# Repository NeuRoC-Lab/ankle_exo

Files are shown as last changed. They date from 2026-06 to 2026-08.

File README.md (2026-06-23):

# ankle_exo
This repository stores the algorithms to operate The OpenExo Styled exoskeleton.

# instructions 

To run the Arduino-Teensy CAN sender receiver test do : 

(1) Connect each of the Arduino R4 and run `pio run -e can_module_arduinos_receiver` or `pio run -e can_module_arduinos_sender` for the receiver arduino and the sender arduino respectively 

(2) Connect one Teensy, run `pio run -e can_module_teensy_receiver` / `pio run -e can_module_teensy_sender` then do same as (1) for the remaining Arduino 

## CubeMars connection with the SN65HVD230 CAN Transceiver module + Arduino Uno R4

Run the Arduino code with `pio run -e arduino_can_cubemars` which will move the motor back and forth 

# A web documentation is available at [this website](https://oscartesniere.com/ankledocs/).

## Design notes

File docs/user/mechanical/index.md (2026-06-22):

Here is the information about the parts printed for the test bench and updates on the mechanical design of the ankle exoskeleton designed by the capstone team.

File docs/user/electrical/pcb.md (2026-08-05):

## The PCB design 

Our ankle exoskeleton design has different requirements than the original OpenExo design. In particular our exoskeleton differs on the following points : 

1. We are using 4x load cells, whereas the original board only accomodates 2x strain gauge amplifiers (INA125U)
2. Our design adds two AMT203 encoders which will most likely be operated over SPI. The original board does include SPI headers near the edge of the board, however the choice of SMT type headers make it incompatible with jumper wires. In addition our encoders work over 5V, which is incompatible with the 3.3V teensy.

Following those specific requirements, we brought the following changes to the board.

- Added two unidirectional voltage shifters for SPI operation at 5V (TXU0104PWR, TXU0304PWR)
-  Added 2 extra strain-gauge amplifiers (INA125U)
-  Used normal pin headers for SPI and included a second CS pin (because there are two encoders)

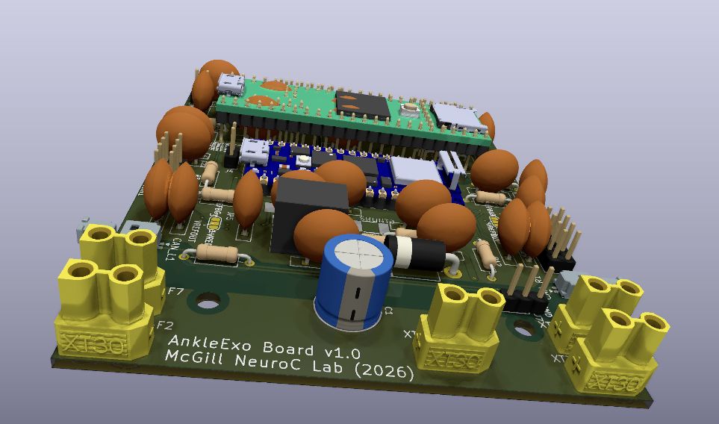
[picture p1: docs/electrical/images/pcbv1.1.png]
The PCB v1.1


A summary of the PCB's role in the ankle exoskeleton is shown in the following diagram : 

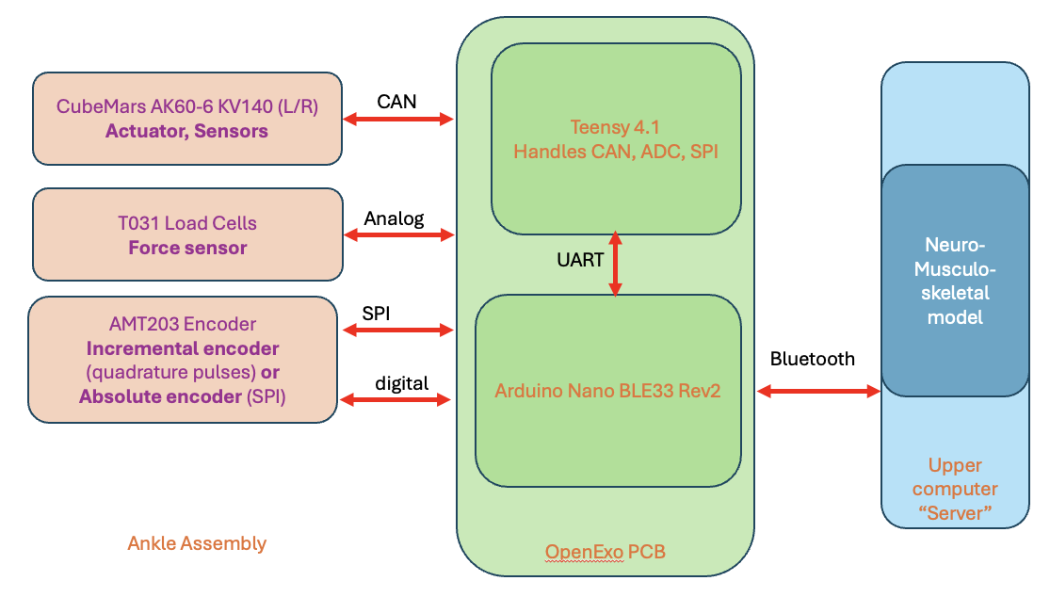
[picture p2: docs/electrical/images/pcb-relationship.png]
PCB diagram


Strain Gauge amplifier design :

The strain gauge amplifier instrumentation amplifier (INA125U) amplifies the voltage difference between the VIN- and VIN+

\[
V_o = IAREFF + G\times (V_+ - V_-)
\tag{1}
\]

Where the gain has expression : \(G = 4 + \frac{60k}{R_g}\)
We kept the original OpenExo gain resistor \(R_g = 470\) thus the gain is about 132.

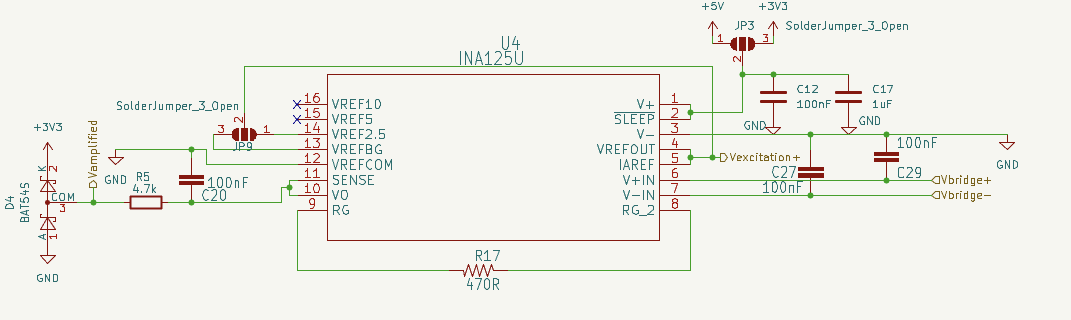
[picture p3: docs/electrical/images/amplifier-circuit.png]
Amplifier Design


In the original OpenExo design, the \(V_{REF}{OUT}\) pin is connected to \(V_{REF}{BG}\) which sets the excitation voltage to the bandgap reference voltage (1.24V).
The load cell datasheet suggests that a minimum of 5V excitation voltage may be used. Even when powering the INA125U the highest excitation voltage that can be achieved is 2.5V. 

For the iteration v1.0 I chose thus to add some flexibility to the choice of \(V_{REF}{OUT}\). Using a 3-pin SolderJumper (JP9,JP3) one can either set the excitation voltage to 1.24V or 2.5V, and the power pin of the IC can be set to 3.3V or 5V (JP3).

In order to allow for the possibility to use \(V_{REF}{5}\) or \(V_{REF}{10}\) I would have to power the chip with a voltage above 5V, or the onboard DC-DC regulator only supplies 5V. Another option could be to connect the INA125U directly to the battery power line but this might introduce some noise and transients from the battery loading the power lines.

The BAT54S is a Diode Array meant to clamp the output voltage in case it exceeds 3.3V, because the Teensy only accepts voltages up to 3.3V.

The `IAREFF` pin sets the voltage offset (see equation(1) ). Since the load cells will only be pulled (tensile force) in one _known_ direction, the polarity of the bridge sensing voltages can be set so that the output voltage will always be below `IARREF`. 
Then we can use a `IAREFF` value near 1.3V, and then the full band range will be between that value and 0V. 

`Load-cell full-scale differential output = sensitivity × excitation voltage`
The datasheet for the T031 load cells specifies 
Sensitivity = 1.0 mV/V nominal
Rated force = 1000 N 

Here is a table that gives the required gain for a given excitation voltage. The highest excitation that can be achieved with the onboard precision reference is 2.5 V, and with a gain of 132, that gives us a full-scale signal of 330 mV.

The desired gain is calculated as \(\text{Target gain} = \frac{3.3 V}{\text{full scale signal}}\)

| Excitation voltage | Load cell full-scale signal | Target gain for 0–3.3 V range | Target gain resistor value |
|-------------------:|----------------------------:|------------------------------:|:--------------------------:|
|            _2.5 V_ |                    _2.5 mV_ |                        _1320_ |          _45.6 Ω_          |
|              3.3 V |                      3.3 mV |                          1000 |           60.2 Ω           |
|                5 V |                      5.0 mV |                           660 |           91.5 Ω           |
|               10 V |                     10.0 mV |                           330 |          184.0 Ω           |

The two parameters that we can modify to increase the full scale signal range are 1) the gain and 2) the bridge excitation voltage

## Force conversion formula

We assume that the load cells are linear. Therefore, the following equality holds:

\[
\frac{V_{diff}(F)}{V_{diff,FS}}
=
\frac{F}{F_{FS}}
\]

where \(FS\) means **full scale**.

For example, the rated full-scale force of the load cell model is typically:

\[
F_{FS} = 1000\,\text{N}
\]

The full-scale differential voltage is given by:

\[
V_{diff,FS}
=
\text{sensitivity}
\times
V_{exc}
\]

Therefore, for an applied force \(F_{applied}\), the output voltage is:

\[
V_o(F_{applied})
=
V_{IAREF}
-
\text{Gain}
\times
\text{sensitivity}
\times
V_{exc}
\times
\frac{F_{applied}}{F_{FS}}
\]

Rearranging the equation:

\[
V_{IAREF} - V_o(F_{applied})
=
\text{Gain}
\times
\text{sensitivity}
\times
V_{exc}
\times
\frac{F_{applied}}{F_{FS}}
\]

Solving for the applied force:

\[
F_{applied}
=
\frac{
\left(
V_{IAREF}
-
V_o(F_{applied})
\right)
F_{FS}
}{
\text{Gain}
\times
\text{sensitivity}
\times
V_{exc}
}
\]

Thus, the applied force can be computed from the measured output voltage as:

\[
\boxed{
F_{applied}
=
\frac{
\left(
V_{IAREF}
-
V_o
\right)
F_{FS}
}{
\text{Gain}
\times
\text{sensitivity}
\times
V_{exc}
}
}
\]

## Effect of the INA125 input-offset voltage

In practice, the INA125 output does not necessarily equal \(V_{\text{IAREF}}\) when the load-cell bridge is perfectly balanced.

One cause is the INA125 input-referred offset voltage, denoted \(V_{\text{OS}}\). The datasheet specifies an input-offset voltage of up to approximately \(250\,\mu\text{V}\). This is a systematic offset, not noise.

The INA125 therefore behaves approximately as though \(V_{\text{OS}}\) were added to the true load-cell differential voltage:

\[
V_{\text{diff}}
=
V_{\text{diff,true}} + V_{\text{OS}}.
\]

The amplifier output becomes:

\[
V_o(F_{\text{applied}})
=
V_{\text{IAREF}}
-
G
\left(
V_{\text{diff,true}} + V_{\text{OS}}
\right).
\]

If the offset is ignored, the raw force calculated from the output voltage is:

\[
F_{\text{raw}}
=
\frac{
\left(
V_{\text{IAREF}} - V_o
\right)
F_{FS}
}{
G\,S\,V_{\text{exc}}
}.
\]

Substituting the amplifier equation gives:

\[
F_{\text{raw}}
=
\frac{
\left(
V_{\text{diff,true}} + V_{\text{OS}}
\right)
F_{FS}
}{
S\,V_{\text{exc}}
}.
\]

Since

\[
V_{\text{diff,true}}
=
S\,V_{\text{exc}}
\frac{
F_{\text{mechanical}}
}{
F_{FS}
},
\]

we obtain:

\[
F_{\text{raw}}
=
F_{\text{mechanical}}
+
\frac{
V_{\text{OS}}F_{FS}
}{
S\,V_{\text{exc}}
}.
\]

The input-offset voltage therefore produces an equivalent force offset:

\[
\boxed{
F_{\text{OS}}
=
\frac{
V_{\text{OS}}F_{FS}
}{
S\,V_{\text{exc}}
}
}
\]

Notice that this equivalent force offset does not explicitly depend on the amplifier gain. The gain increases both the useful signal and the output-referred offset by the same factor.

## Effect of residual cable tension

When the ankle exoskeleton is assembled, the Bowden cable may already apply a nonzero preload to the load cell. This residual force is denoted:

\[
F_{\text{residual}}.
\]

The total mechanical force measured by the load cell is then:

\[
F_{\text{mechanical}}
=
F_{\text{applied}}
+
F_{\text{residual}},
\]

where \(F_{\text{applied}}\) is the additional force of interest.

Including both the INA125 offset and the residual cable tension gives:

\[
F_{\text{raw}}
=
F_{\text{applied}}
+
F_{\text{residual}}
+
F_{\text{OS}}.
\]

Therefore,

\[
\boxed{
F_{\text{applied}}
=
F_{\text{raw}}
-
F_{\text{residual}}
-
F_{\text{OS}}
}
\]

or, written directly in terms of the measured output voltage:

\[
\boxed{
F_{\text{applied}}
=
\frac{
\left(
V_{\text{IAREF}} - V_o
\right)
F_{FS}
}{
G\,S\,V_{\text{exc}}
}
-
F_{\text{residual}}
-
\frac{
V_{\text{OS}}F_{FS}
}{
S\,V_{\text{exc}}
}
}
\]

## Practical zeroing procedure

In practice, \(F_{\text{residual}}\) and \(V_{\text{OS}}\) do not need to be determined separately. Both effects can be removed by recording the amplifier output after the exoskeleton has been assembled and placed in its reference unloaded state.

Let \(V_{o,0}\) be the output voltage measured in this reference state. It includes both the INA125 offset and the residual Bowden-cable tension:

\[
V_{o,0}
=
V_{\text{IAREF}}
-
G
\left[
S\,V_{\text{exc}}
\frac{
F_{\text{residual}}
}{
F_{FS}
}
+
V_{\text{OS}}
\right].
\]

When an additional force \(F_{\text{applied}}\) is present:

\[
V_o
=
V_{\text{IAREF}}
-
G
\left[
S\,V_{\text{exc}}
\frac{
F_{\text{residual}} + F_{\text{applied}}
}{
F_{FS}
}
+
V_{\text{OS}}
\right].
\]

Subtracting the two equations eliminates \(V_{\text{IAREF}}\), \(V_{\text{OS}}\), and the residual mechanical preload:

\[
V_{o,0} - V_o
=
G\,S\,V_{\text{exc}}
\frac{
F_{\text{applied}}
}{
F_{FS}
}.
\]

The corrected applied force is therefore:

\[
\boxed{
F_{\text{applied}}
=
\frac{
\left(
V_{o,0} - V_o
\right)
F_{FS}
}{
G\,S\,V_{\text{exc}}
}
}
\]

This equation assumes that the INA125 output decreases as the applied tensile force increases. If the output increases with force because the load-cell polarity is reversed, use:

\[
\boxed{
F_{\text{applied}}
=
\frac{
\left(
V_o - V_{o,0}
\right)
F_{FS}
}{
G\,S\,V_{\text{exc}}
}
}
\]

## ADC constraint limitation 

The teensy's ADC (for PCB versions v1.1.0 and earlier) and the Arduino Nano's ADC (for PCB versions v1.1.1 and above) can read analog voltages *from 0V to 3.3V* 

Therefore \(0 \le V_o(F_{\text{applied}}) \le 3.3\)

\[ \iff \frac{V_{\text{IAREF}}\cdot F_{\text{FS}}}{G\cdot S  \cdot V_{exc}} \ge F_{\text{applied}} \ge \frac{(V_{\text{IAREF}}-3.3)\cdot F_{FS}}{G\cdot S  \cdot V_{exc}}\]

An example for the following configuration : 

| Gain (G) | Maximum tensile force \(F_{\min}\) | Maximum compressive force \(F_{\max}\) |
| -------: |-----------------------------------:|---------------------------------------:|
|     6004 |              \(-83.28~\mathrm{N}\) |                  \(+26.65~\mathrm{N}\) |
|     1204 |             \(-415.28~\mathrm{N}\) |                 \(+132.89~\mathrm{N}\) |

Note that compression and tension are defined visually the following way. 

Because the motor actively pulls on the load cells, the expected tensile-force range is greater than the expected compressive-force range. The INA125U reference voltage was therefore selected so that a larger portion of the ADC input range is allocated to tensile-force measurements.

The value of \(V_{\mathrm{IAREF}}\) was set to \(2.5~\mathrm{V}\). With an ADC input range of \(0\text{–}3.3~\mathrm{V}\), this provides \(2.5~\mathrm{V}\) of output range below \(V_{\mathrm{IAREF}}\) and \(0.8~\mathrm{V}\) above it. This choice is appropriate if tensile loading causes the INA125U output voltage to decrease. If tensile loading instead causes the output voltage to increase, \(V_{\mathrm{IAREF}}=1.24~\mathrm{V}\) would provide greater tensile-force headroom.

The higher-output range of the INA125U was not used because the amplifier output is not inherently limited to the ADC’s maximum allowable input voltage of \(3.3~\mathrm{V}\). An excessive load could therefore overdrive, and potentially damage, the ADC input unless an additional clamping or protection circuit is used.

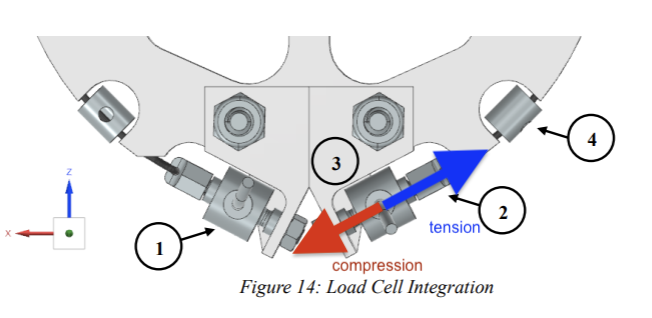
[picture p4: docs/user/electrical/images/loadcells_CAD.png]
load cell CAD

## Pinout of the PCB 

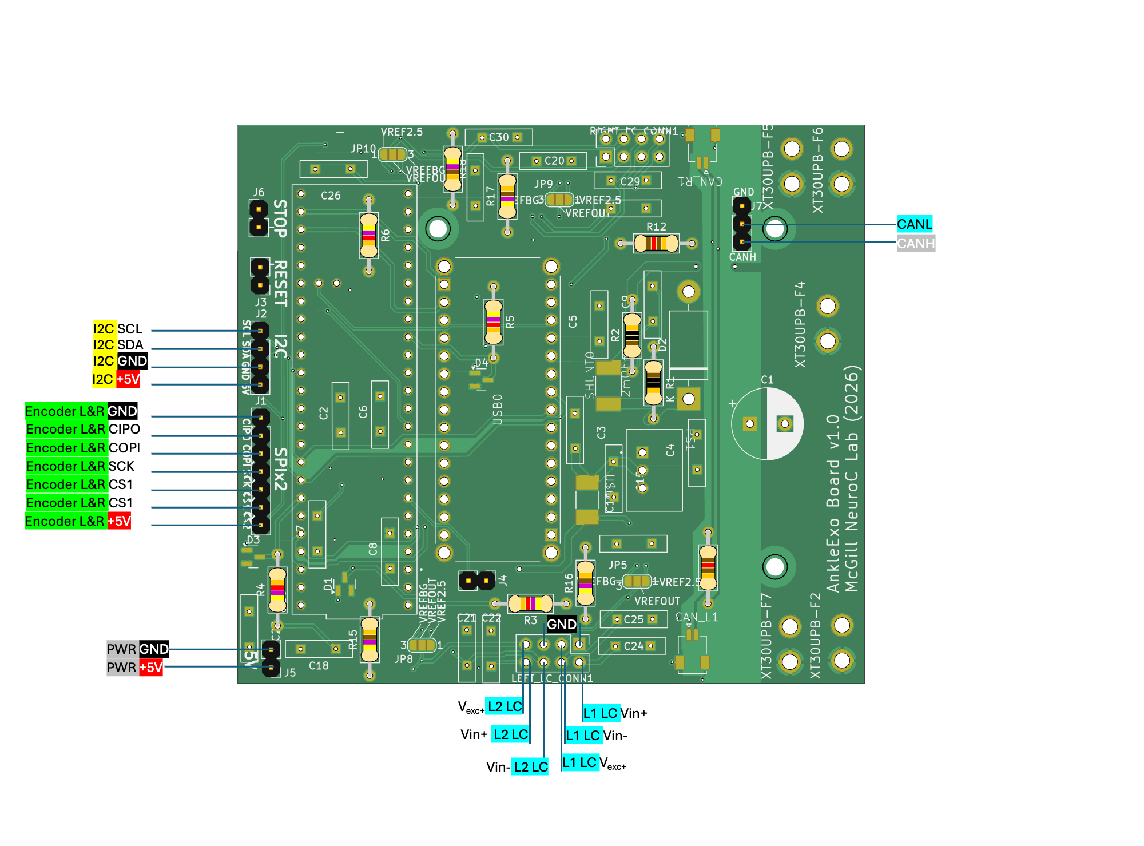
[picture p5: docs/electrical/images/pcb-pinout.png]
Pinout


Pinout for the load cells connectors : 

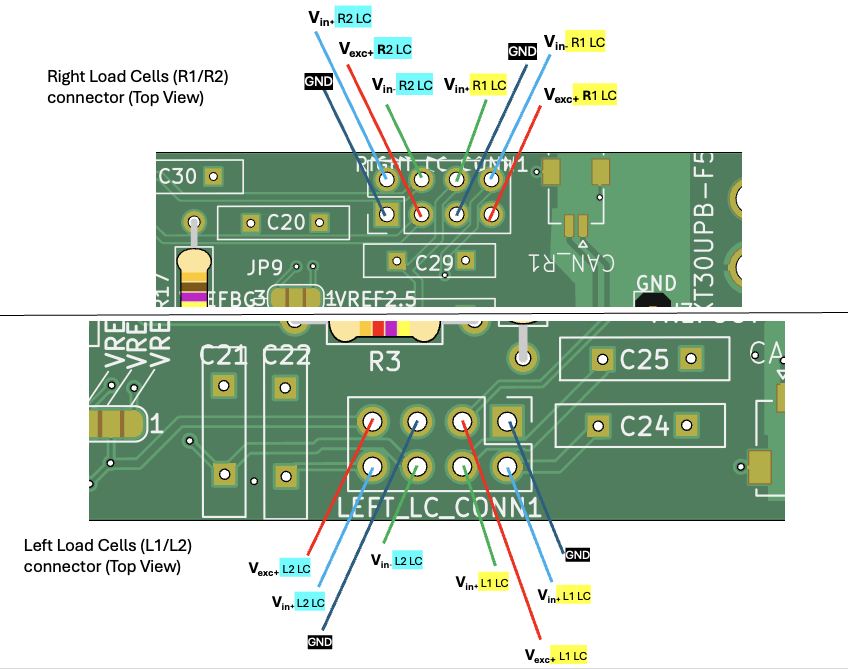
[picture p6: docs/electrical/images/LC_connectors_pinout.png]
Load Cells Pinout

## PCB changelog 

#### 26/06 (version 1.0.0)

* Refactored labels for INA solder jumpers by aligning the labels on a "45degrees" plane so that we can distinguish those labels from other things on the board (clearer for reading)
* Added a solder jumper for INA excitation voltage to choose between the INA voltage reference (2.5v/BG) or 5V from PCB regulator
* Added a solder jumper to choose whether to connect the Teensy's VIN to the board (so that we can use USB)

#### 03/07 (version v1.0.1)

* Modified the Teensy 4.1 footprint to include two 1x24 PinSocket rows so that we can include the pin socket soldering into PCBA for JLCPCB
* Added a status LED for the 5V power line
* Make sure to check for unconnected zones 
* Modified the pinout order for the SPI header (it is now from left to right `GND`,`SCK`,`COPI`,`CIPO`,`CS1`,`CS2`,`5V`)
* Make sure to check the option `Subtract soldermask from silkscreen` : this will tell KiCad to _automatically remove silkscreen graphics/text wherever they overlap exposed copper pads_ which might otherwise cause manufacturing issues
* **MAIN PATCH : **  Re-routed the TXU304 and TXU0104 input  / output pins to resolve mismatch in version v1.0.0. The inputs were misconnected to outputs which made the SPI non functioning on version v1.0.0. _The SPI bus has fixed direction ports (COPI, SCK, CS go from controller to peripheral, while CIPO goes from peripheral to controller) but the order was mismatched in version 1.0.0_

Before the patch `.1`
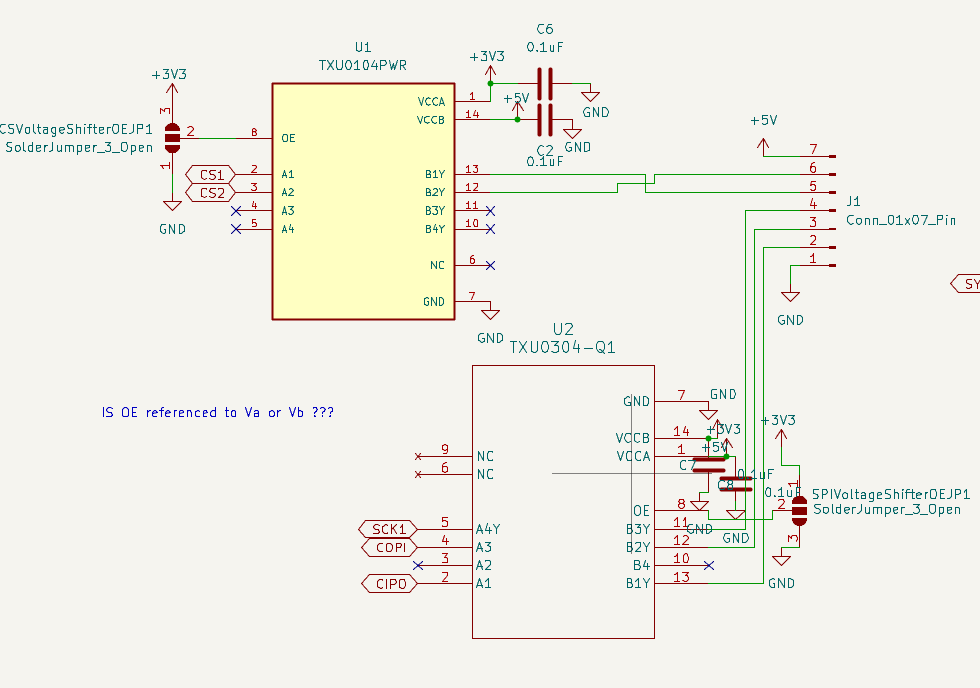
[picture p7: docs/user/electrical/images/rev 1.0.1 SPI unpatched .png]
SPI before patch 1.0.1

After the patch `.1`
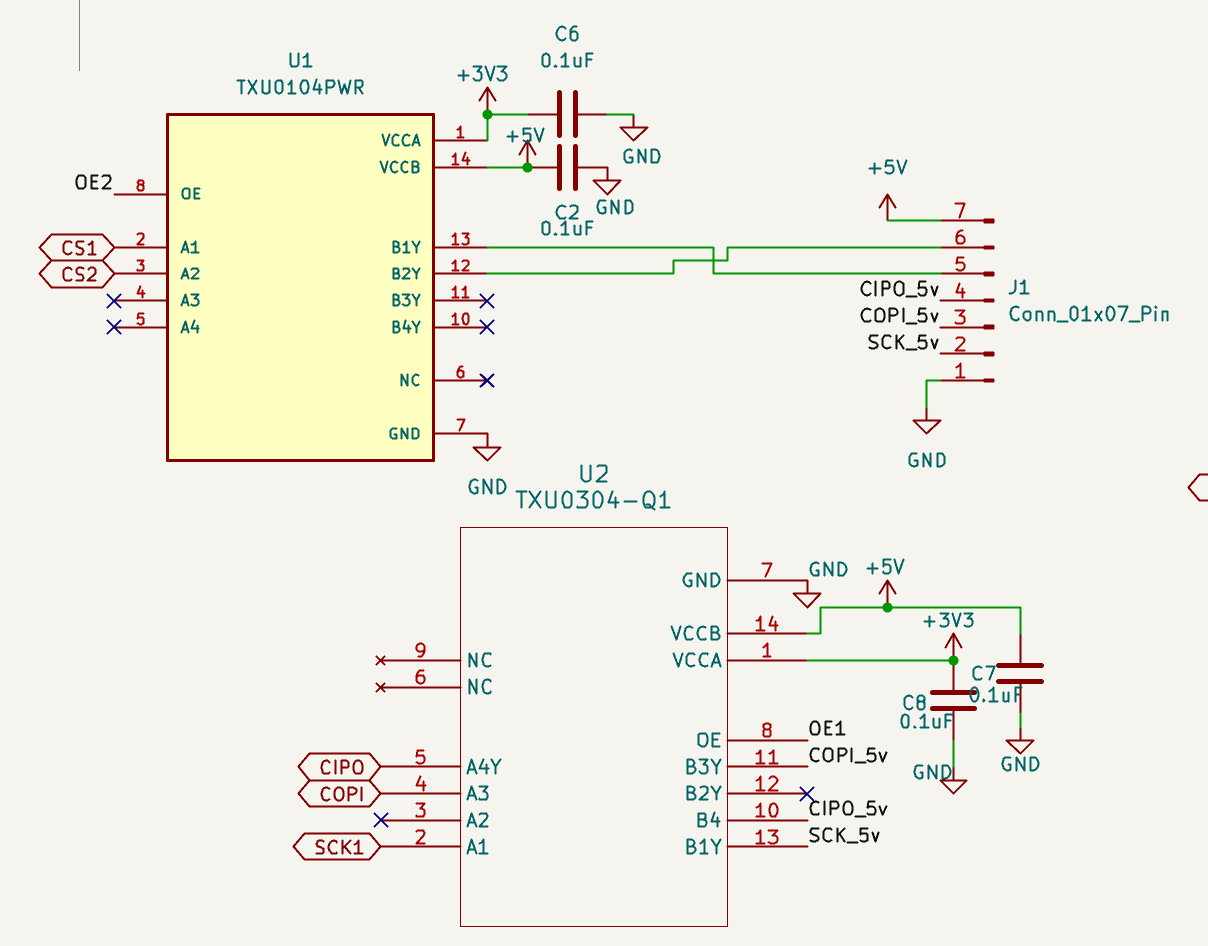
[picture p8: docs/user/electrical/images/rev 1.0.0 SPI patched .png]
SPI after patch 1.0.1


#### 04/07 (version v1.0.1)
* connected excitation voltage outputs of the 4 INA125U to Teensy's Analog inputs so that the Teensy can ensure the INA125Us are properly wotking and that these match the settings in Board.h

#### 17/07 (version v1.1.0)

* Replaced erroneous Arduino Nano (BX00028=Nano Every) symbol+footprint with corresponding model (the BX00071=Nano BLE33 R2). Check that the older versions (<v1.1.0) are not affected, especially UART b/w Teensy and Nano
* Redesigned the load cell sampling circuit to use the Arduino Nano's builtin SAADC in differential mode. The advantages are :
  * The Teensy 4.1's analog pins are known to be noisy so the Nano naturally becomes a more stable option 
  * The differential mode (where IN+=Vexc and IN-=INA125U output) simplifies the `Board.h` configuration. The code no longer needs to know what voltage is each IAREF at, since the differential ADC extracts the differential voltage 
  * The differential mode also improves signal integrity by rejecting the common-mode noise picked up by the lines on the PCB.
  * The differential mode eliminates any IAREF voltage drifts / offsets _ACCROSS_ and _WITHIN_ all four INA125Us. The code assumed that the IAREF voltages were exactly 2.5V or 1.24v but in practice soldering quality and trace impedance can affect that by introducing some variability between the IAREF of each respective INA125U
  * The Arduino Nano's SAADC features a PGA stage which makes this setup more flexible to changing `Rg` gain resistors. We can optimize the dynamic range to improve resolution.
* Redesigned the `LEFT_LC_CONN` and `RIGHT_LC_CONN` pinout so that 1) they are identical (versions < v1.1.0 had distinct pinouts) 2) they are _SYMETRICAL_ which means the 2x4 connector can safely be flipped, only the load cell will be swapped. 
PCB assembly list : 

https://jlcpcb.com/help/article/how-to-generate-the-bom-and-centroid-file-from-kicad

### 23/07 (v1.1.0)

* Fixed XT30 connector pin mismatch on kicad which resulted in \(V_{batt}\) and \(GND\) nets not being actually electrically connected to the XT30 pins on the board. For this I renamed the pin names on the symbol from "P" and "N" to 2 and 1 respectively, as required in the footprint 
* Replaced the imported Teensy symbol which made some pins not properly connected 
* Remade Solder jumper annotations pertaining to each of the four amplifiers more consistently (INA_PWR_xx, INA_EXC_xx, INA_REF_xx) for 1,2,3,4
* Converted 3-pins solder jumpers to 2-pins solder jumpers to avoid harming Nano ADC by connecting it to 5V

### 25/07 (v1.1.1)
* Replaced the P78E05-1000 with a [Würth Elektronik pin-compatible equivalent](https://www.we-online.com/components/products/datasheet/173010535.pdf?srsltid=AfmBOoqXnjU4nN0V3SnTI2uxeimFK-YTeBzOPeDcg751XvU_F-sQBI_F).
  * MINOR ROUTING FIX (schematics/pcb) : While the pinout for P78E05-1000 is 1-Vin, 2-GND, 3-Vout, the v1.1.0 board that was obtained through JLCPCB (the second one) had 3) have pin 2 and 3 swapped and pin 1 not actually connected to Vin (battery). The routing was redone properly, and bulk capacitors were placed at input and output of the DC-DC converter

* MINOR WIRING FIX (schematics/pcb) : The BAT54S clamping diode array was replaced with a more accurate one (BAS70-04). The cathode and anode were swapped in the old version, which has been fixed when adding the replacement diode array.
* The Teensy 4.1's footprint and symbol was modified and I principally removed unused THT pins like VUSB,T+/T-,D+/D- and otherswhich would have overlapped with some components under the Teensy

<iframe
src="https://oscartesniere.com/3dviewer/viewer/embed.html#model=https://oscartesniere.com/3dviewer/models/AnkleExov1_1_0.glb"
title="AnkleExo PCB v1.1.0"
width="100%"
height="700"
style="
display: block;
width: 100%;
border: 1px solid #cccccc;
border-radius: 8px;
"
loading="lazy"
allowfullscreen>
</iframe>

<iframe
src="https://oscartesniere.com/3dviewer/viewer/embed.html#model=https://oscartesniere.com/3dviewer/models/AnkleExov1_1_1.glb"
title="AnkleExo PCB v1.1.1"
width="100%"
height="700"
style="
display: block;
width: 100%;
border: 1px solid #cccccc;
border-radius: 8px;
"
loading="lazy"
allowfullscreen>
</iframe>

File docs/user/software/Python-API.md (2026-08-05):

## Python API

A self-contained Python API has been written to interface the exoskeleton from a BLE compatible device in Python.

The file to use is `src/python-scripts/SingleLeg/single-exo.py`

The main `Exoskeleton` class supports context management framework, which internally handles connection to and disconnection from the BLE-enabled Arduino Nano

A typical script skeleton loooks like this : 

```python
from single-exo import Exoskeleton
# assumes your python file is in `src/python-scripts/SingleLeg`

with Exoskeleton() as ankle_exo:
    # your code goes here, connection and disconnection is being handled internally 
    pass
```

Please see the available functions to read from the sensors and to send commands to the Motors.

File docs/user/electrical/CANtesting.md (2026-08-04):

### Validation of the onboard CAN

An external CAN module was used to test the proper operation of the CAN bus. The CAN bus was then made of two nodes : the SN65HVD230 transceiver on the PCB, and another SN65HVD230 transceiver on the external module.
> Note that because the PCB already includes a 120 \(\Omega\) termination, you MUST unsolder the 60 \(\Omega\) resistor on the external CAN transceiver module (use a voltmeter to identify which resistor to remove among the two. The other one is usually 10k \(\Omega\))

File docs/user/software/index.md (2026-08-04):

The software layer works as follows : 
* The Teensy 4.1 and Arduino Nano BLE33 Rev2 make part of the PCB software stack
* The main "server" running torque moment generation is a separate entity 

## Teensy and Arduino Nano programing environment and workflow :

### Platformio 

We chose platformio (abbreviated `pio`) for it's seamless integration with both the Arduino Nano and the Teensy.
The Arduino IDE supports both boards and architecture, however pio provides useful features key to our development : 
- All-in-one compile-upload-monitor pipeline for fast development
- Configurable environments to distinguish scripts that are to be run on the Teensy vs those to be run on the Arduino. The environments are defined in `platformio.ini`
- Easier project management for multiple sketches. The CLI-based nature of pio allows us to easily integrate version control (git) 

To run an environment (ex `myenv`) run in the same directory as `platormio.ini` the following command : `pio run -e myenv`

To monitor a specific device (`myport`) over the serial monitor run `pio device monitor --port myport`. To get the list of available ports run `ls /dev/cu*`

#### Platformio setup 

Platformio can be installed as a standalone application [`platformio cli`](https://docs.platformio.org/en/latest/core/index.html) which gives access to a command line interface for running direct commands. It is lightweight and does not rely on an overlaying IDE, however you must be familiar with CLI and know the commands to run for compiling/uploading/monitoring

Platformio is also available as an integration into popular IDEs like VScode, CLion [`platformio-ide`](https://docs.platformio.org/en/latest/integration/ide/pioide.html#pioide). We recommend using VScode because the graphical interface is easy to navigate through. 

To install platformio on vscode, locate the platformio plugin in the marketplace 

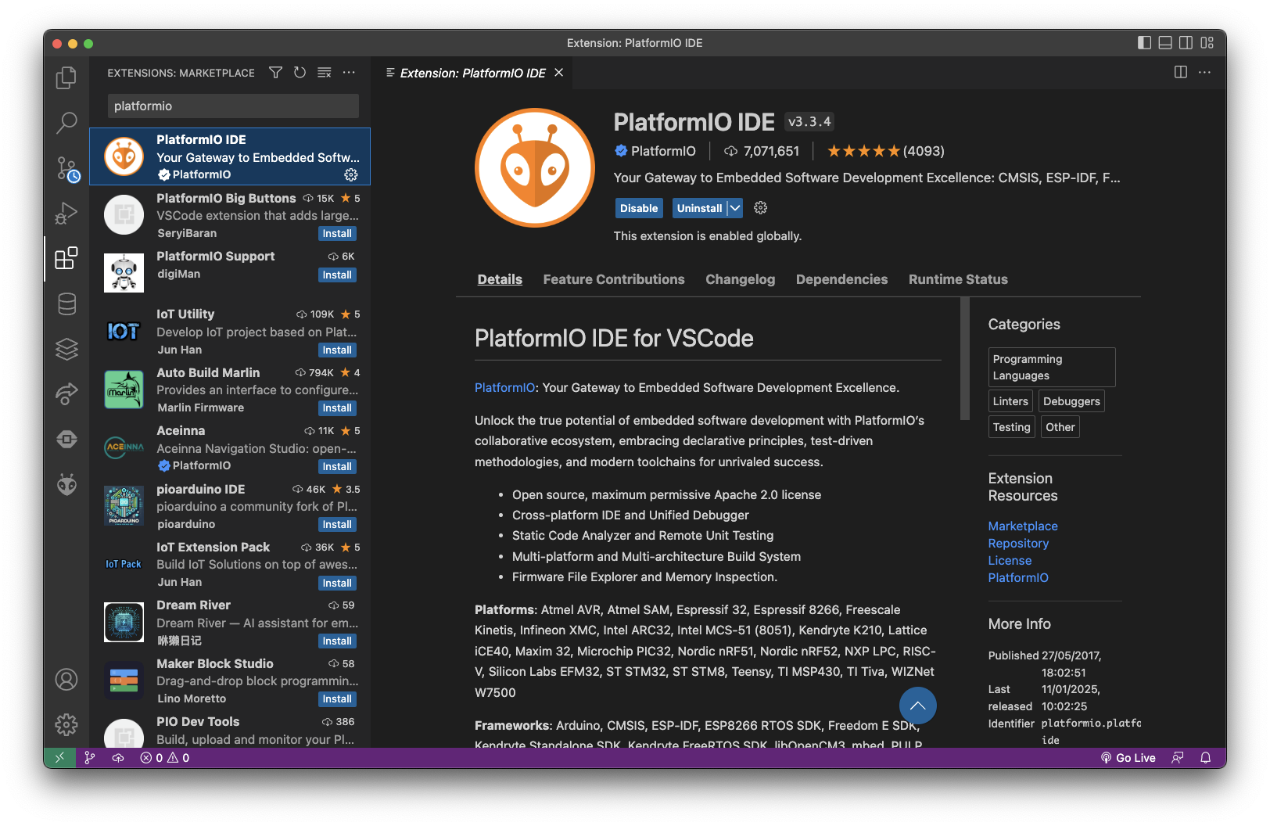
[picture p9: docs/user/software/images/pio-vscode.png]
VScode installation of platformio


To install platformio on CLION, follow the instructions [here](https://www.jetbrains.com/help/clion/platformio.html#debug-prj)

### Setting up the Arduino IDE for compiling, uploading and monitoring the Teensy 4.1

_For reference : https://www.pjrc.com/teensy/tutorial.html_

The Arduino IDE doesn't provide a built-in board manager for the Teensy 4.1 board, so the first time setting up the Arduino IDE for the project you'll need to add this custom board manager URL from PJRC :

In the `Additional boards manager URLs` (`File > Preferences`) text box paste the following URL : 

`https://www.pjrc.com/teensy/package_teensy_index.json`

Wait for the IDE to install the board package, then make sure to choose the port labelled `Teensy 4.1`. Another port will show up when you plug the Teensy on your computer, but do not choose this one. 

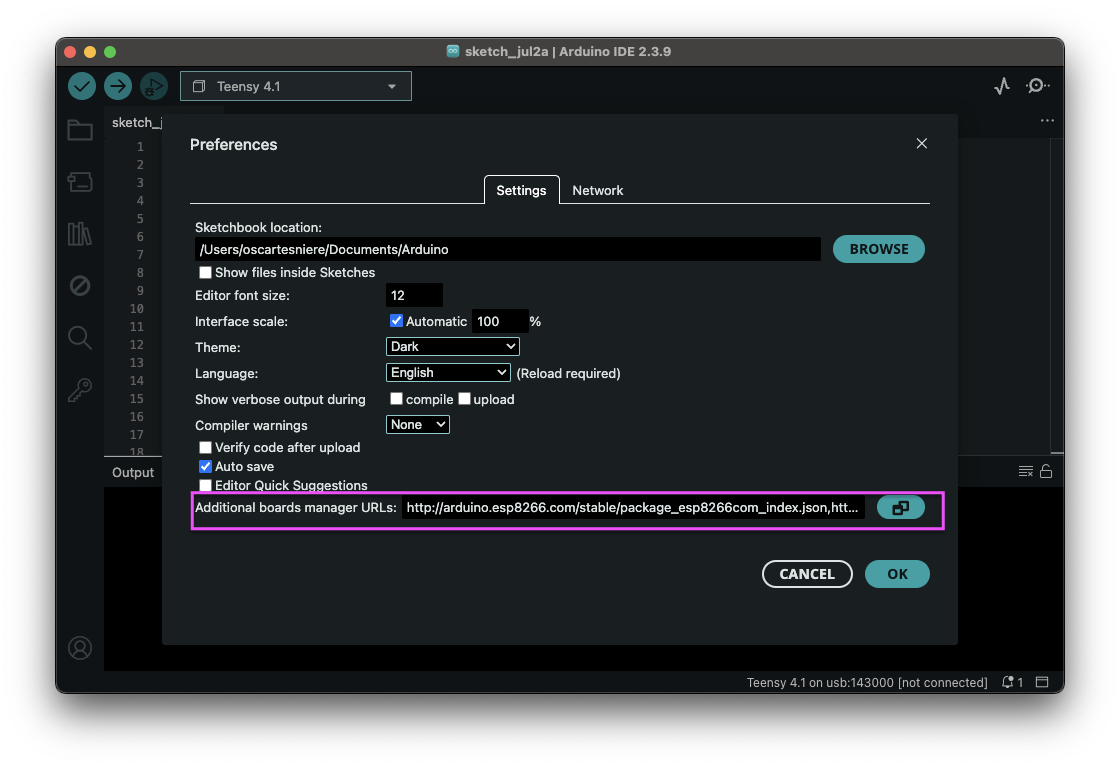
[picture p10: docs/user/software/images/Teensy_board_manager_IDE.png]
Port selection


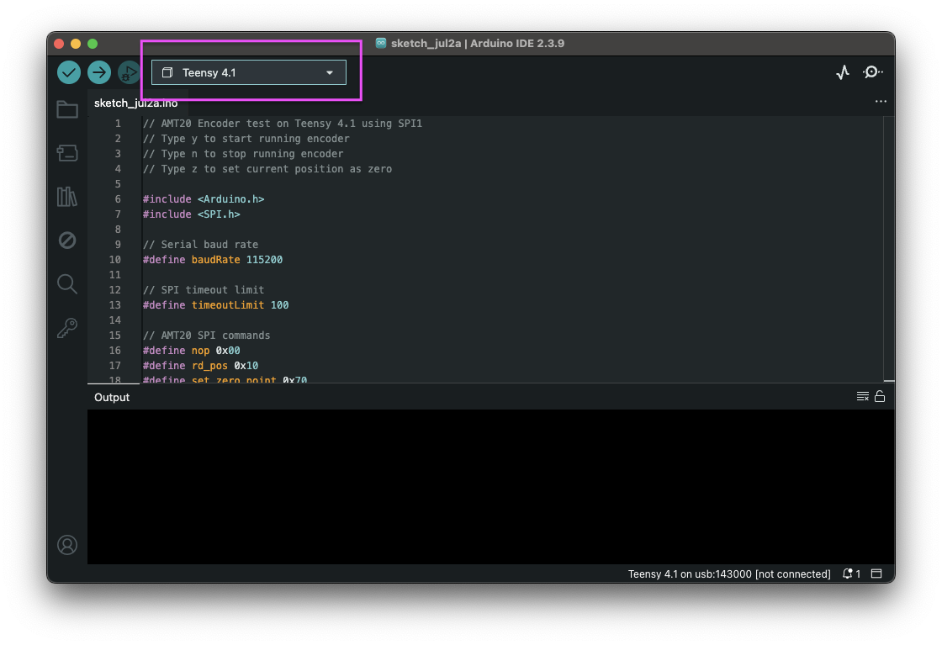
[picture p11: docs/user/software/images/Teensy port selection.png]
Board Manager setup


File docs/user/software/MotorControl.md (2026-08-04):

### Motor control theory 

The user-commanded position, velocity, torque, proportional gain, and derivative gain are restricted to a commanded operating range, referred to as the **software constraint set**, (\mathcal{S}).

A second, extended admissible range is defined as the **running constraint set**, (\mathcal{R}). This range represents the absolute limits within which the motor is permitted to operate based on its measured state. The two constraint sets satisfy

\(\mathcal{S}\subseteq\mathcal{R}\)

and, when the running constraint is strictly wider than the software constraint,

\(\mathcal{S}\subsetneq\mathcal{R}\)

Consequently, a user command must satisfy

\(\mathbf{u}_{\mathrm{cmd}}\in\mathcal{S}\),

whereas the measured motor state must remain within

\(\mathbf{x}_{\mathrm{motor}}\in\mathcal{R}.\)

The region (\mathcal{R}\setminus\mathcal{S}) provides a recovery margin that accommodates tracking error, system dynamics, and externally imposed motion while preventing the user from directly commanding the motor near its absolute operating limits.

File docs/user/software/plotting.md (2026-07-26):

## Reference Page for Real-Time Sensors Plotting Scripts

The real-time plotting of the exoskeleton sensors and motors is achieved using Python 
To check for the list of ports in CLion IDE, use python -m serial.tools.list_ports

The result for a one leg setup can be found through the unified.py script under software/src/python-scripts
It plots 6 graphs: 

- encoder angle
- encoder velocity
- cable tension 1
- cable tension 2
- motor position
- motor velocity

Challenges encountered and solution process:

1. Find a way to control the motor while the plot is running

- UI slider
  - Pros: easy to use for testing purposes
  - Cons: only temporarily needed feature
- Import threading to send commands via the terminal
  - Pros: same way to control motor as the motor script alone
  - Cons: not practical at all if printing data on the terminal 
- Using Teensy and Nano at the same time (plot from reading Nano data, control motor by sending commands to Teensy)

2. Plot fast and smoothly enough

- Replace 
  raw = ser.readline().decode(errors="ignore").strip()
  with
  while ser.in_waiting:
  raw = ser.readline().decode(errors="ignore").strip()
- Telemetry library?

3. Noise in one load cell caused by crosstalk and wiring/PCB issues

4. Encoder noise when motor is turned on but with a zero velocity

5. Encoder random spikes caused by invalid reading returns the uint_16_max
- When there is an invalid reading, plot the previous valid reading

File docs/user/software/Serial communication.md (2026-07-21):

### Serial communication between the Teensy 4.1 and the host computer

!!! info "Note for later iterations" 
    The use of Serial communication (UART) seemed like an ideal choicen for us because 1) it is easier to implement than SPI 2) we can easily transpose it to Bluetooth later on

## Teensy payload formating

A typical packet from the Teensy looks like this, as seen from the Serial Monitor

```python
 {
    "LLC1":2.512674,
    "LLC2":2.532015,
    "RLC1":0.032234,
    "RLC2":0.030623,
    "LENC":28671,
    "RENC":65295,
    "MOTORS":[{"MTR_ID_DEC":2,"MTR_POS_RAD":0.476654,"MTR_VEL_RADS":0.032967,"MTR_TRQ_NM":-0.032967,"MTR_TEMP_DEG":64,"MTR_ERR_DEC":0}]
}
```
the main fields are : 

* `LLCx` : left load cell x (1 or 2)
* `RLCx` : right load cell x (1 or 2)
* `LENC` : left encoder count
* `RENC` : right encoder count
* `MOTORS` : motors field, contains a list of motor telemetry data (one per each) with keys `MTR_ID_DEC`, `MTR_POS_RAD`, `MTR_VEL_RADS`, `MTR_TEMP_DEG`, `MTR_ERR_DEC`

On python, you need to do the following to retrieve data (See `testUart.py` for an application)

1. Parse the line from the Serial with `line = Serial.readLines('\n')` 
2. Parse the JSON to convert the string into a dictionnary-like array with `packet = json.loads(line)`
3. Extract individual fields with `.get()` method. For example :
```python
left_load_cell = packet.get("LLC1")  # left load cell 1 voltage
right_encoder = packet.get("LENC") # left encoder count
```

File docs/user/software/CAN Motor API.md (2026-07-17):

### Usage of `CANMotorMIT.h` and `ServoCANMotor.h` erre— CAN Motor API

1. In both MIT and Servo modes, auxiliary libraries such as `SerialMotorControl.h` use the generic `CANController` type name for the selected motor controller.

   Therefore, after including the appropriate controller header, define `CANController` as an alias for the platform-specific implementation.

   For MIT mode with a Teensy 4.1:
```Cpp
#include "CANMotorMIT.h"
using CANController = CANMotorMIT_Teensy;  
```

   When using an Arduino UNO R4 instead:

```Cpp
using CANController = CANMotorMIT_Renesas;
```

   For Servo mode with a Teensy 4.1:

```Cpp
#include "ServoCANMotor.h"
using CANController = ServoCANMotor_Teensy;
```

   When using an Arduino UNO R4 instead:

```c++
using CANController = ServoCANMotor_Renesas;
```

2. In MIT mode specifically, the user must define:

    * the software command constraints;
    * the motor running constraints.

   These values should be configured in `MotorConfig.h`.

3. Create a `MotorCmd` object that will store the commands sent to the motor.

   Example for MIT mode:

```c++
MotorCmd motor1Cmd {
      .position = 0.0f,
      .velocity = 0.0f,
      .torque = 0.0f,
      .kp = 0.0f,
      .kd = 0.0f
   };
```

4. Instantiate a `CANController` object.

   Example for MIT mode:

```c++
CANController motor(
       MOTOR_ID,
       &motorParams,
       &motorSoftwareConstraints,
       &motorRunningConstraints,
       motor1Cmd,
       printRate
   );
```

   The arguments are:

    * `MOTOR_ID`: the motor CAN ID. It can be checked or configured using the CubeMars Upper Computer software.
    * `motorParams`: the nominal motor communication parameters.
    * `motorSoftwareConstraints`: the limits applied to commands before they are sent to the motor.
    * `motorRunningConstraints`: the safety limits checked against motor feedback.
    * `motor1Cmd`: the `MotorCmd` object containing the current user command.
    * `printRate`: the motor status will be printed to the Serial Monitor once every `printRate` received frames.

   The Servo-mode constructor may use a different set of arguments because software and running constraints are currently specific to the MIT controller.

5. Include `SerialMotorControl.h` to enable control through the serial interface:

```c++
   #include "SerialMotorControl.h"
```

   Include this header only after the `CANController` alias and motor object have been defined, if the library depends on them.

6. Create the serial controller object:

```c++
   SerialMotorControl serialControl(Serial, motor1Cmd, motor);
```

7. In `setup()`, initialize the motor controller:

```c++
motor.begin();
```

   Reset and enable the motor using:

```c++
   if (!motor.resetMotor()) {
       Serial.println("Failed to start motor");
   } else {
       Serial.println("Motor started successfully");
   }
```

8. In `loop()`, call the following functions to process CAN communication and serial commands:

```c++
   void loop()
   {
       motor.update();
       serialControl.update();

       delay(10);
   }
```

   The delay is currently required for reliable serial command handling and should not be removed until the timing behavior has been investigated.

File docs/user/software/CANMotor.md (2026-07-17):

## Software layout for the project 

### CANMotor class

The `CANMotor` class is the main class used to interface the motor. 

As of now because we are having issues interfacing the encoders with the Teensy over SPI (voltage conversion related) I gave the possibility 
for the user to control the AnkleExo PCB using 1) the Teensy and 2) with the Arduino Uno R4. It is necessary to split the implementation for the Uno R4 and the Teensy 4.1 because these two boards use different CAN Controller libraries.
The Arduino uses `Arduino_CAN.h` while the Teensy currently uses `FlexCAN_T4`. For that reason I created two subclasses for each board so that one can use one or the other board as they wish.

Note that because only the Teensy 4.1 and Arduino UNO R4 boards have an integrated CAN controller other regular boards like the Arduino UNO R3 _cannot_ be used for this class.

For the wiring, please refer to `board.h` and the `electrical` section of this documentation. It differs from board to board.

A representative OOP diagram of the `CANMotor` class and it's two subclasses `CANMotor_Teensy41`, `CANMotor_Renesas` is shown below

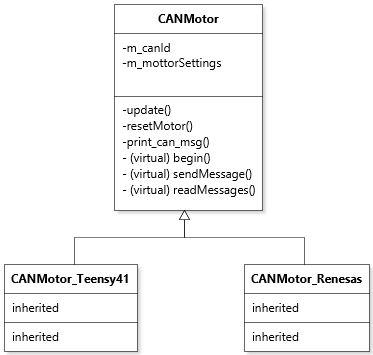
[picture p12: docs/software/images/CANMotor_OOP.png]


To run the unified CAN controller example code (`CAN_unified.cpp`) you will need to run the pio environment `CAN_teensy41` or `CAN_uno_r4` depending on which board you are using. 
As a reminder, the general format to run an environment in platformio is `pio run -e yourenvname` where `yourenvname` is the target environment. 

#### Design update (25/06)

After the Servo mode was successfully tested on June 24th we are now implementing a separate class for the MIT and Servo mode. Those supercless are `CANMotorMIT` (MIT mode) and `ServoCANMotor` (Servo mode). Note that these two classes need to been validated again 

| Class                   | Mode | Board          | Platformio Environment        |
|-------------------------|-----:|:---------------|-------------------------------|
| `CANMotorMIT_Teensy`    |  MIT | Teensy 4.1     | `pio run -e MIT_CAN_teensy41` |
| `CANMotorMIT_Renesas`   |  MIT | Arduino Uno R4 | `pio run -e MIT_CAN_uno_r4`   |
| `ServoCANMotor_Renesas` | Servo | Arduino Uno R4 | `pio run -e Servo_CAN_uno_r4` |
| `ServoCANMotor_Teensy`  | Servo | Teensy 4.1     | NOT IMPLEMENTED YET           |

The following commands can be run (rightmost command) to execute the MIT/Servo demo code on the Teensy/Arduino Uno R4. 
Note the following : 

* You must wire the CANTX/CANRX wires accordingly to the Teensy or Arduino UNO R4.

* For the Arduino 

  | OpenExo PCB                     | Arduino |
  |---------------------------------|--------:|
  | CANTX _through voltage divider_ |     D10 |
  | CANRX                           |     D13 | 
  | GND                             |     GND | 
  | 3.3V                            |   3.3V  | 

* For the Teensy

| OpenExo PCB                     | Arduino |
|---------------------------------|--------:|
| CANTX  |     D22 |
| CANRX                           |     D23 | 
| GND                             |     GND | 
| 3.3V                            |    3.3V | 

#### Serial communication 

The serial communication to control the motor works as follow : 

##### MIT mode

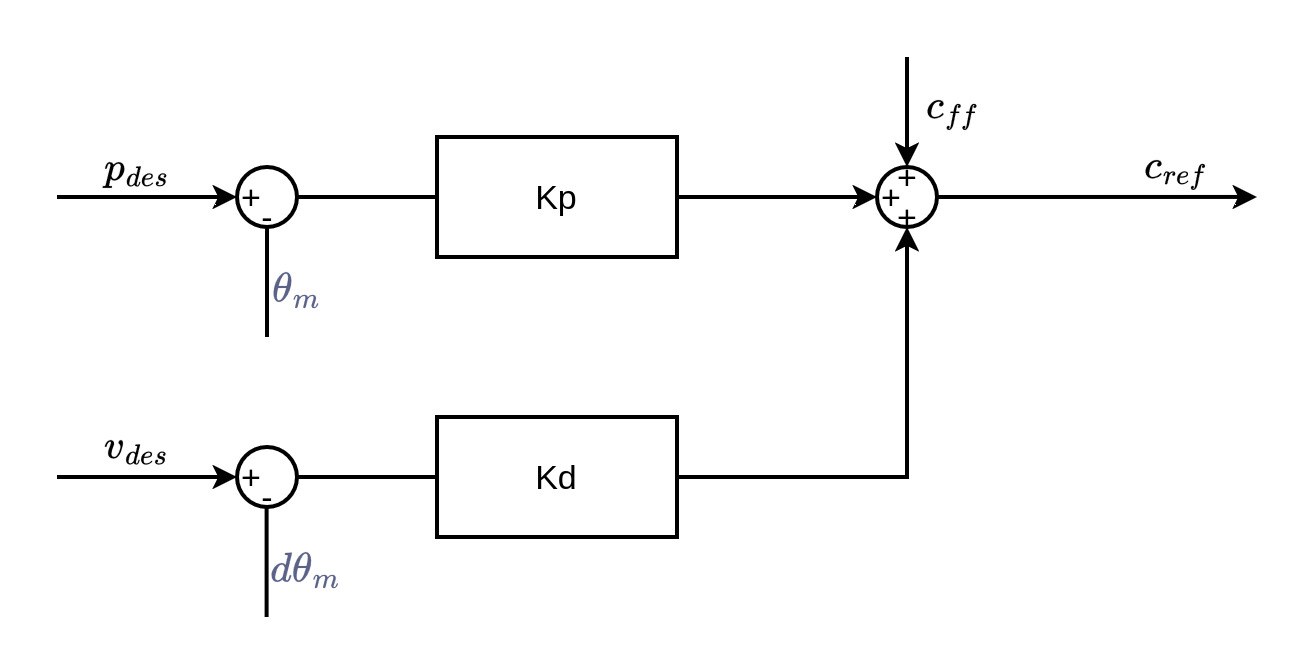
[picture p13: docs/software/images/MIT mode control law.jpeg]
MIT control law from SITODRIVE


\(c_{ff}\) value is usually the sum of the current required to offset the friction of the actuator and the current value calculated by the robot dynamics

When the kp and kd values are both 0, the rotational stiffness and damping are both 0, which is equivalent to the current mode, and the phase current can be directly controlled:

Increasing the feedforward torque \(c_{ff}\) will offset the necessary torque to overcome the static friction. As a consequence the motor is set into motion easier. 

References from [sito drive for the MIT actuator control mode](https://docs.sitodrive.com/Joint_Actuator_User_Documentation/Detailed_explanation_of_control_mode/MIT_mode)

Note : setting kd to wero will make the motor oscillate about the target position which is not recommended

* `start id xx` : start the motor 
- To enable the control loop, after a "crash" wherein the motor disables itself after a fault was detected

* `stop id xx` : disable the control loop (the motor is in idle mode, and keeps sending telemetry data but there is no actuation. note you can still set MIT parameters)
- To exit idle mode, enter the `start` command. 

* `zero id xx` : resets the motor's encoder position to 0 at the current position. 

`set` | `id xx`: 

  - `pos x.x` : position (in radians from -12.0 to +12.0)
  - `vel x.x` : velocity (in radians/s from -45.0 to +45.0)
  - `kp x.x` : proportional gain (for position)
  - `kd x.x` : derivative gain (for velocity)
  - `trq x.x`  : feedforward torque (be careful with it when using the motor with no load attached to the shaft as it will spin freely while accelerating)

_Note that the order the parameters are given does not matter. One / more parameter can be updated at once_
##### Servo Mode

`set` | `id xx`  :

  - `duty x.x` : set duty cycle mode
  - `current x.x` : set current mode (proportional to torque T = kI)
  - `brake x.x` : set brake current mode
  - `rpm x.x` : set rpm mode
  - `pos x.x` : set position mode
  - `pos x.x rpm x.x acc x.x` : set position velocity acceleration loop mode
  -  `origin 0` : set encoder origin

  - _Note that only ONE mode can be active at a time_ (WAIT MAYBE NO ACTUALLY?)

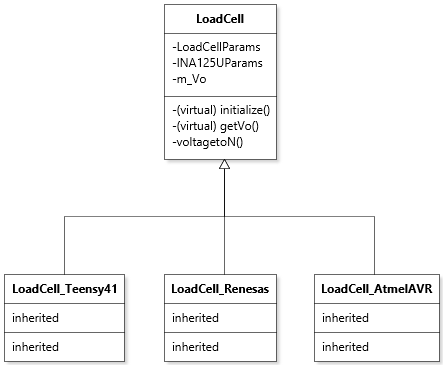
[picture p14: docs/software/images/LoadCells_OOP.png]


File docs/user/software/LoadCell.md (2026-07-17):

### LoadCell class

The `LoadCell` class is the main class used to interface the motor.

For the same reason as mentionned earlier, I gave the possibility to run this code on different board achitectures, namely 1) The Arduino UNO R3 (AtmelAVR), 2) The Arduino UNO R4 (Renesas) and 3) the Teensy 4.1
Because the `LoadCell` class simply requires to read a voltage from an Analog pin all of the boards can be used. However the implementation slightly differs from board to board. For example, the Teensy can only support voltages in the 0-3.3V range while Arduino UNO R3/R4 have an extended ADC input voltage range of 0-5V.
Please keep that in mind when setting up the strain gauge amplifier as driving voltages beyond the GPIO limit can permanently damage the board.

Specific boards may be used for specific needs :

1. The Arduino UNO R3 is the simplest option and most straightforward. I recommend starting with this
2. All boards can be used to interface the integrated INA125U on the [PCB](/electrical/pcb) however _pay attention to the voltage ranges_. Assert statements during compile time will throw errors if the theoretical `Vo` range goes beyond the ADC voltage range.

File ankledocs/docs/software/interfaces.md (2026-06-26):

## Software layout for the project 

### CANMotor class

The `CANMotor` class is the main class used to interface the motor. 

As of now because we are having issues interfacing the encoders with the Teensy over SPI (voltage conversion related) I gave the possibility 
for the user to control the AnkleExo PCB using 1) the Teensy and 2) with the Arduino Uno R4. It is necessary to split the implementation for the Uno R4 and the Teensy 4.1 because these two boards use different CAN Controller libraries.
The Arduino uses `Arduino_CAN.h` while the Teensy currently uses `FlexCAN_T4`. For that reason I created two subclasses for each board so that one can use one or the other board as they wish.

Note that because only the Teensy 4.1 and Arduino UNO R4 boards have an integrated CAN controller other regular boards like the Arduino UNO R3 _cannot_ be used for this class.

For the wiring, please refer to `board.h` and the `electrical` section of this documentation. It differs from board to board.

A representative OOP diagram of the `CANMotor` class and it's two subclasses `CANMotor_Teensy41`, `CANMotor_Renesas` is shown below

OOP Diagram

To run the unified CAN controller example code (`CAN_unified.cpp`) you will need to run the pio environment `CAN_teensy41` or `CAN_uno_r4` depending on which board you are using. 
As a reminder, the general format to run an environment in platformio is `pio run -e yourenvname` where `yourenvname` is the target environment. 

#### Design update (25/06)

After the Servo mode was successfully tested on June 24th we are now implementing a separate class for the MIT and Servo mode. Those supercless are `CANMotorMIT` (MIT mode) and `ServoCANMotor` (Servo mode). Note that these two classes need to been validated again 

| Class                   | Mode | Board          | Platformio Environment        |
|-------------------------|-----:|:---------------|-------------------------------|
| `CANMotorMIT_Teensy`    |  MIT | Teensy 4.1     | `pio run -e MIT_CAN_teensy41` |
| `CANMotorMIT_Renesas`   |  MIT | Arduino Uno R4 | `pio run -e MIT_CAN_uno_r4`   |
| `ServoCANMotor_Renesas` | Servo | Arduino Uno R4 | `pio run -e Servo_CAN_uno_r4` |
| `ServoCANMotor_Teensy`  | Servo | Teensy 4.1     | NOT IMPLEMENTED YET           |

The following commands can be run (rightmost command) to execute the MIT/Servo demo code on the Teensy/Arduino Uno R4. 
Note the following : 

* You must wire the CANTX/CANRX wires accordingly to the Teensy or Arduino UNO R4.

* For the Arduino 

  | OpenExo PCB                     | Arduino |
  |---------------------------------|--------:|
  | CANTX _through voltage divider_ |     D10 |
  | CANRX                           |     D13 | 
  | GND                             |     GND | 
  | 3.3V                            |   3.3V  | 

* For the Teensy

| OpenExo PCB                     | Arduino |
|---------------------------------|--------:|
| CANTX  |     D22 |
| CANRX                           |     D23 | 
| GND                             |     GND | 
| 3.3V                            |    3.3V | 

#### Serial communication 

The serial communication to control the motor works as follow : 

##### MIT mode
* `start id xx` : start the motor (it will otherwise remain deaf to commands)
* `stop id xx` : stop the motor and put it in idle mode
* `zero id xx` : set the motor's zero

`set` | `id xx`: 

  - `pos x.x` : position (in radians from -12.0 to +12.0)
  - `vel x.x` : velocity (in radians/s from -45.0 to +45.0)
  - `kp x.x` : proportional gain (for position)
  - `kd x.x` : derivative gain (for velocity)
  - `trq x.x`  : feedforward torque (be careful with it when using the motor with no load attached to the shaft as it will spin freely while accelerating)

_Note that the order the parameters are given does not matter. One / more parameter can be updated at once_
##### Servo Mode

`set` | `id xx`  :

  - `duty x.x` : set duty cycle mode
  - `current x.x` : set current mode (proportional to torque T = kI)
  - `brake x.x` : set brake current mode
  - `rpm x.x` : set rpm mode
  - `pos x.x` : set position mode
  - `pos x.x rpm x.x acc x.x` : set position velocity acceleration loop mode
  -  `origin 0` : set encoder origin

  - _Note that only ONE mode can be active at a time_
### LoadCell class

The `LoadCell` class is the main class used to interface the motor. 

For the same reason as mentionned earlier, I gave the possibility to run this code on different board achitectures, namely 1) The Arduino UNO R3 (AtmelAVR), 2) The Arduino UNO R4 (Renesas) and 3) the Teensy 4.1
Because the `LoadCell` class simply requires to read a voltage from an Analog pin all of the boards can be used. However the implementation slightly differs from board to board. For example, the Teensy can only support voltages in the 0-3.3V range while Arduino UNO R3/R4 have an extended ADC input voltage range of 0-5V. 
Please keep that in mind when setting up the strain gauge amplifier as driving voltages beyond the GPIO limit can permanently damage the board.

Specific boards may be used for specific needs : 

1. The Arduino UNO R3 is the simplest option and most straightforward. I recommend starting with this
2. All boards can be used to interface the integrated INA125U on the [PCB](/electrical/pcb) however _pay attention to the voltage ranges_. Assert statements during compile time will throw errors if the theoretical `Vo` range goes beyond the ADC voltage range.

OOP Diagram

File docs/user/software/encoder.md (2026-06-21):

# Encoders 

the AMT20 encoders series comes in two version : incremental encoders (through quadrature outputs) or absolute encoders (through SPI). Our encoder model (The AMT203-V) is an absolute position encoder and is thus interfaced over SPI.

## Absolute encoder : 

The encoder features en internal register which updates the absolute position at a rate of 40us (25 kHz). It is interfaced over SPI

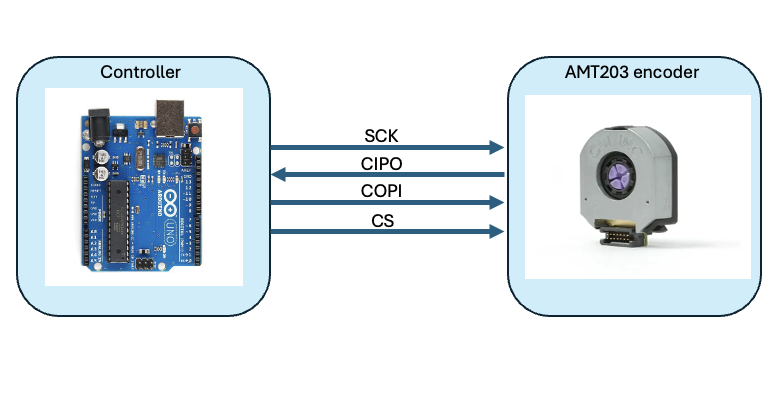
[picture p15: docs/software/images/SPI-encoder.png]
SPI Wiring diagram


The encoder is both 3.3V and 5V tolerant, however the CIPO (controller-in peripheral out) pin will be 5V voltage level, therefore when using a 3.3V logic MCUs (like the Teensy or the Nano) you MUST shift down the voltage from CIPO before connecting it to the MCU. 

When using an Arduino Uno R3 / R4, this is not an issue. However a typical setup for a 3.3V MCU is : 

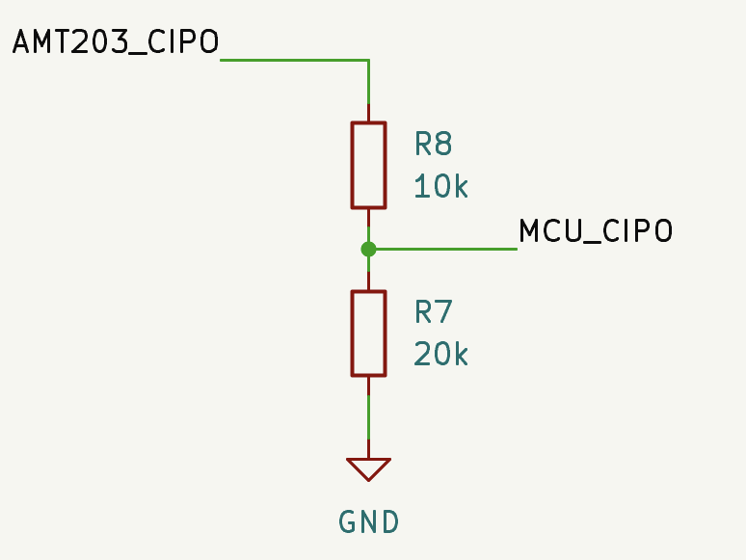
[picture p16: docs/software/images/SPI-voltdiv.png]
Voltage divider for CIPO


Using the voltage divider equation : 

\[
V_{out} = V_{in} \times \frac{R_2}{R_1 + R_2} \iff
V_{out} = 5 \times \frac{20k}{10k + 20k}  \iff
V_{out} = 5 \times \frac{20}{30} \iff
V_{out} = 3.33V
\]

We can use setup a shared SPI bus and assign a CS pin to each of the two encoders (left and right) so that only one encoder uses the SPI bus at a time. This means that to sync the two encoders's update we have to reduce the overall update rate by a factor of 2. 

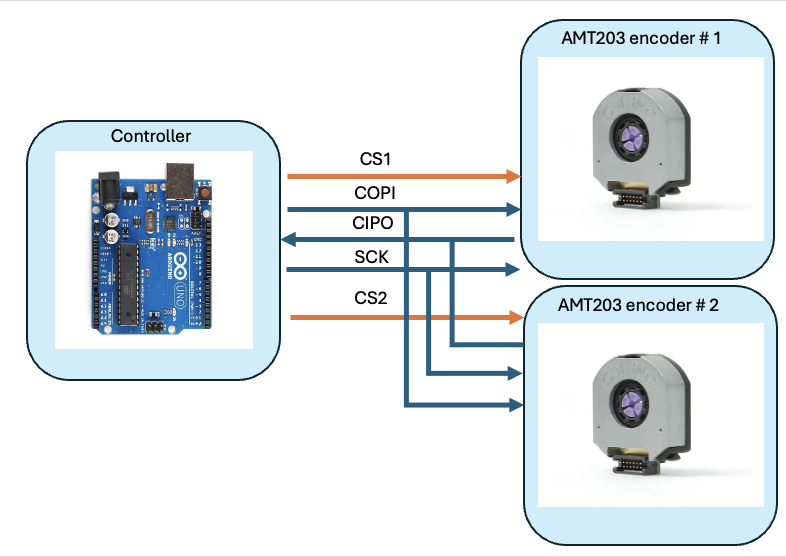
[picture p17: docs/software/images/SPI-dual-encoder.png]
SPI dual encoder configuration


### Arduino UNO SPI pinout for testing the encoder

When using the Arduino UNO R3/R4 to interface the encoder over SPI, use the following table to connect the SPI pins (CIPO/COPI/CS/SCK)

| COPI (Cont. Out Per. In) | CIPO (Cont. In Per. Out) | SCK (Serial Clock) | CS (Chip Select) |
|-------------------------:|-------------------------:|-------------------:|:----------------:|
|                      D11 |                      D12 |                D13 |       D10        |

## Incremental encoder : 

We also have access to the encoder's raw quadrature outputs (A/B/Z). The outputs A/B are used to count the increments of the encoder and tell the direction of rotation to update the counter (A→B vs B→A) while Z is the index, and generates a pulse once every full rotation

All of the Teensy 4.1's digital pins support interrupts, which makes the incremental encoder method a good candidate for fast encoder resolution and reading.

Somehow the quadrature signals don't work ???

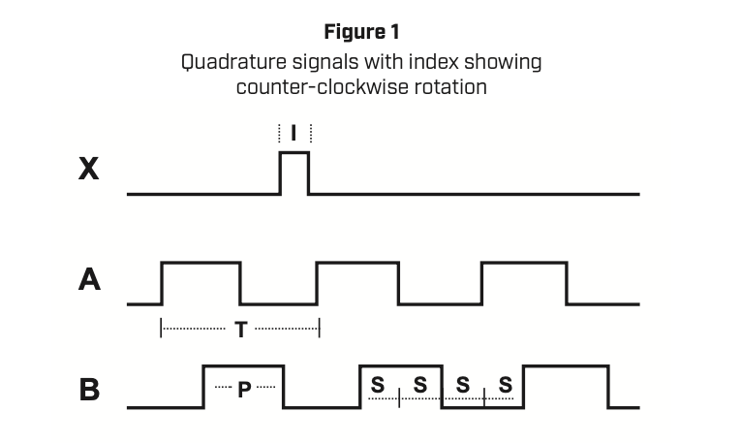
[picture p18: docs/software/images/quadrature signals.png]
Quadrature signals


## Ressources 

The encoder datasheet can be found here : [encoder datasheet](../files/amt20-datasheet.pdf)

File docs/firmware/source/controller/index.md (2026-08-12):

# Creating your custom motor controller and registering it. 

## Programming guidelines

Motor-related controllers should be added onto {ref}`Driver.h <motorcontrollers-h>` which contains all the existing controller classes such as 

```{doxygenclass} MotorCommandTask
:project: framework
```

```{doxygenclass} MotorCanReceiver
:project: framework
```

```{doxygenclass} MotorMetaCommandTask
:project: framework
```

```{doxygenclass} JointLimitController
:project: framework
```

```{doxygenclass} TransparentModeController
:project: framework
```

The Controller class you are designing _MUST_ inherit from the `ITask` class

The declaration should look as follows : 

Note : 
* `[TopicTypeX]` is a placeholder for the type of the topic, for example `EncoderPositions` for the encoder topic. 
* `[topicXMember]` is a placeholder for the name of the member holding a reference to the Topic `Topic<[TopicTypeX]>`
```c++
class YourController final : public ITask { 

public: 

    YourController(Topic<[TopicType1]>& [topic1Member], 
                   Topic<[TopicType2]>& [topic2Member],
                 /* etc... */ 
                  )  
                 : 
                m_topic1Member(topic1Member),
                m_topic2Member(topic2Member),
                /* etc... */       
                { }                  
```
...
```c++
void update(uint32_t nowUs) override
    {
    // your update logic goes here
    // the nowUs parameter can be used to track the current time ( micros() )
    }
```
...
```c++
private:
Topic<[TopicType1]>& [topic1Member];
Topic<[TopicType2]>& [topic2Member];
/*etc*/
// and define any other private fields as well
};
```

For more information about the Topic class, have a look at its definition in {ref}`MessageBus.h <topic-class>`

### Registering the controller to activate it

Once your controller is defined, you need to register it properly in `main.cpp`

1. Instanciate a controller object in the global scope (outside `setup()` or `loop()`). For e.g to create an instance of `JointLimitController`
```c++
JointLimitController jointController(
    encoderTopic,
    loadCellTopic,
    leftMotorTopic,
    leftMotorCommandTopic,
    leftMotorMetaCommandTopic
);
```

2. Add the controller to the `Scheduler` as follows :
Using our `JointLimitController` example again, you can add the `jointController` to the scheduler by adding : 
```c++
scheduler.add(jointController);
```

This will ensure the `jointController::update()` method gets called at every loop iteration. To rate-limit the execution of the `update()` function you need to implement a non-blocking delay inside the update() function itself. For example : 

```c++
    void update(uint32_t nowUs) override
    {
        static constexpr uint32_t PERIOD_US = 10'000;

        if (nowUs - m_previousUs < PERIOD_US)
            return;

        m_previousUs += PERIOD_US;
    ... // rest of update logic goes here
    }
```

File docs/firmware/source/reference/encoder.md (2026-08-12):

# Reading encoder positions

The framework uses an `EncoderDriver` to manage the two joint encoders.

The driver handles initialization, validation of encoder readings,
rollover correction, and conversion from counts to degrees.

## Encoder driver

```{doxygenclass} EncoderDriver
:project: framework
```

The important part for normal application code is that the driver
must first be initialized.

```{doxygenfunction} EncoderDriver::begin
:project: framework
```

After initialization, call `sample()` whenever a new encoder
measurement is required.

```{doxygenfunction} EncoderDriver::sample
:project: framework
```

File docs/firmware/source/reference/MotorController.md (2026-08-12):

(motorcontrollers-h)=

# `MotorControllers.h`

```{doxygenfile} MotorControllers.h
:project: framework
```

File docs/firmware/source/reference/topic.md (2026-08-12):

(topic-class)=

# `Topic` class

```{doxygenclass} Topic
:project: framework
:members:
:private-members:
:undoc-members:
```

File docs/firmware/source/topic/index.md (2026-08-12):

## Topic guidelines

A topic acts as a node that holds a snapshot of a variable, it can be updated (`.publish()`) and its latest value can be probed with (`.latest()`).

### Motivations

Instead of having each controller sample from the peripherals (encoder, load cells) directly, we chose to design a uniform access method that periodically updates its internal state so that controllers can access the latest value held by the Topic. 

A topic implements : 
* `.latest()` : returns the latest value (snapshot) in the state store
* `.publish(T value)` : updates the state store with the given `value`
> Note : for motor topics the method is slightly different and has signature `.apply(MotorCmd& cmd)`

For more informations look at {ref}`the Topic reference page <topic-class>`

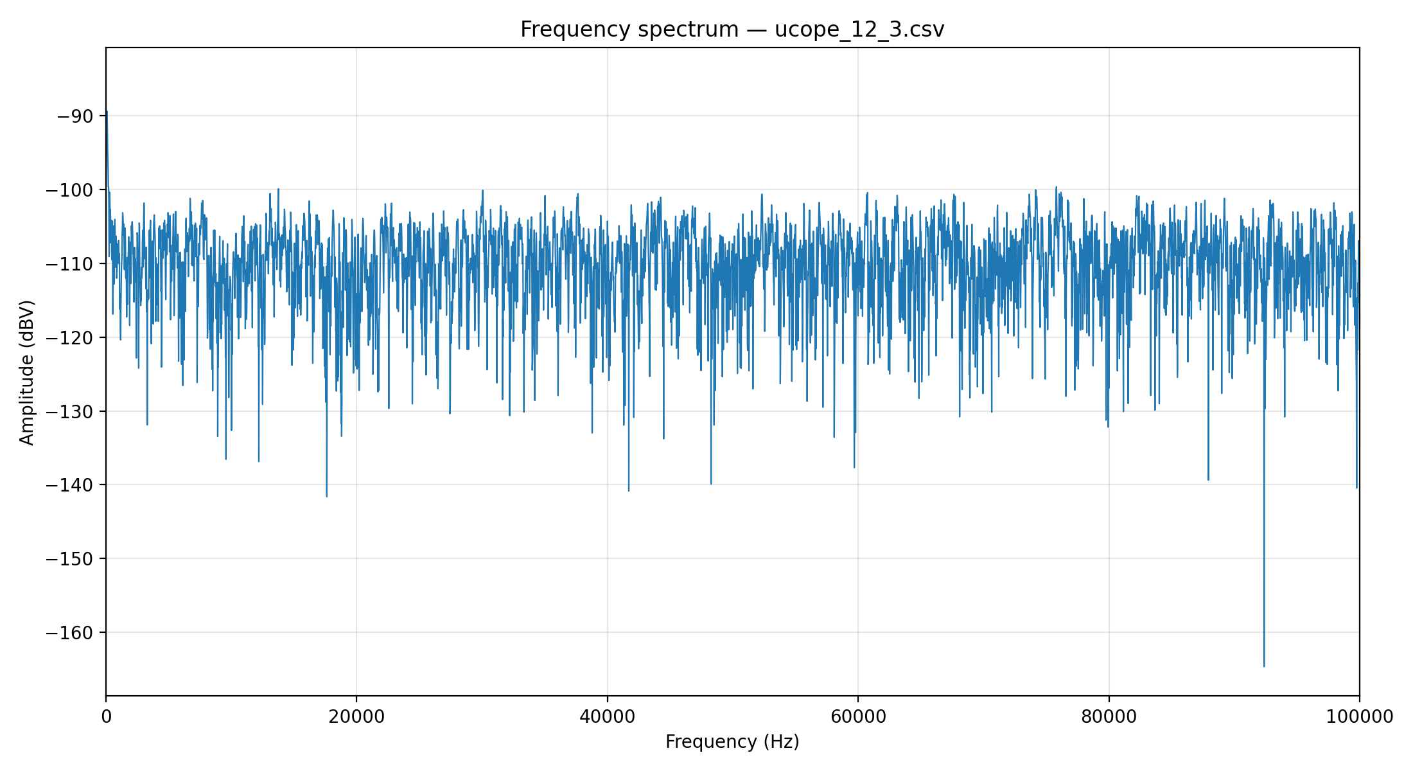
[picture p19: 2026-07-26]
software/src/python-scripts/spectrum.png

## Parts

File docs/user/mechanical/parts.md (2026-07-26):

## Ankle Exoskeleton Mechanical Design Modifications

The original mechanical design assembly can be found in the NeuroC Lab OneDrive folder following:

### Pulley Cable Attach

The original pulley cable attach design had multiple issues:

- the screws used to assemble them to the pulley were touching, leaving no free space and thus making assembling the load cells difficult
- no fillets to reinforce the thin walls
- the side thin wall was only present on one side, making the part unnecessarily asymmetric (takes longer to adjust)

The new design takes the following into consideration:

- the cable stays tangential to its first point of contact to the pulley
- there is some free space in between the 2 screws
- the increased dimensions still make sure that no part will touch the floor
- fillets added in inner edges
- printed using CFRP (?)

Original Part: Original PulleyCableAttach
Revised Part: Revised PulleyCableAttach

## Waist Belt Design

General design considerations:

- One belt that can be used for unilateral and bilateral exoskeletons
- Can hold the weight of the exoskeleton + batteries + hardware with minimal load on the user

### PCB Pocket

The PCB design can be found here:

Specific design considerations: 

- Hold PCB and PCB case
- Allow space for cables and connections

The CAD file for the PCB pocket can be found here: Belt PCB Pocket

### Battery Pockets (4)

Specific design considerations:

- Hold one or two batteries at a time
- Can attach and detach from belt
- Allow space for two large cables
- Thermal safety

The CAD file for the battery pocket can be found here: Belt Battery Pocket

## Test Bench Parts

### Fixing the Motors (3D Print)

The current part takes into all these considerations:

- uses the holes on the motor's back to screw the motor to the part
- leaves ample space at the bottom for the motor cable connections
- ensures unobstructed motor rotation facing outward the test bench
- minimizes vibrations at high torque/velocity motor testing operations
- holds the weight of the motor
- fixes to the test bench with screws through one hole and one slot

Motor Test Bench Part DOESN'T WORK YET; ADD IMAGE IN ISOMETRIC VIEW

The CAD file can be found in SolidWorks using: [Motor Test Bench Part](../CAD-files/motor-mount.sldprt)

### Fixing The Exo Horizontally (3D Prints)

The current part takes into all these considerations:

- leaves space to adjust by hand the two bowden cable knobs
- keeps the exoskeleton horizontally placed without slipping or rotations
- minimizes non-necessary plastic use while ensuring enough part strength
- fixes to the test bench with screws through one hole and one slot

The following consists of 3 parts:

- The base, which is fixed to the test bench through 2 screws
- The cap, which sandwiches the exo in between itself and the base. It is fixed to the base through 2 screws and 2 nuts
- The clip, which is placed in between the knobs to prevent sliding along the exoskeleton's parallel axis

Each of the he CAD files can be found in Siemens NX (TO UPLOAD)
Base: [Ankle Test Bench Part - Base](../CAD-files/ankle-mount-base.prt)
Cap: [Ankle Test Bench Part - Cap](../CAD-files/ankle-mount-cap.prt)
Clip: [Ankle Test Bench Part - Clip](../CAD-files/ankle-mount-clip.prt)

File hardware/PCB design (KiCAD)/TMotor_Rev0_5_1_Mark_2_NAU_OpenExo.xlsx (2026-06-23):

Reference | Value | Footprint | Datasheet | Qty | DNP | Exclude from BOM | Exclude from Board
C1 | C_Polarized_US | Capacitor_THT:CP_Radial_D10.0mm_P5.00mm | ~ | 1
C2 C6 C7 C8 "0.1uF" | Capacitor_THT:C_Disc_D10.5mm_W5.0mm_P5.00mm | ~ | 4 |  |  |  |  | NOTE : will get them from Factory
C3 C5 C9 C15 C18 C19 C20 C21 C22 C23 C24 C25 C26 C27 C28 C29 C30 | 100nF | Capacitor_THT:C_Disc_D10.5mm_W5.0mm_P5.00mm |  | 17
C4 | 0.33uF | Capacitor_THT:C_Disc_D10.5mm_W5.0mm_P5.00mm |  | 1
C10 C11 C12 C13 | 100nF |  | ~ | 4 |  |  |  | NOTE : will get them from the factory
C14 C16 C17 C31 | 1uF |  | ~ | 4 |  |  |  | NOTE : unsolder those from the PCB
CAN_L1 | CAN_R1 | 5015680207 | TMotor_Rev0_5_1_Mark_2_NAU_OpenExo:MOLEX_5015680207 |  | 2
D1 D3 D4 D5 | BAT54S | Package_TO_SOT_SMD:SOT-23 | https://www.diodes.com/assets/Datasheets/ds11005.pdf | 4
D2 | 1N5400 | Diode_THT:D_DO-201AD_P15.24mm_Horizontal | http://www.vishay.com/docs/88516/1n5400.pdf | 1
INA219 | ~ | TMotor_Rev0_5_1_Mark_2_NAU_OpenExo:D8_TEX |  | 1
J1 | Conn_01x07_Pin | Connector_PinHeader_2.54mm:PinHeader_1x07_P2.54mm_Vertical | ~ | 1
J2 | Conn_01x04_Pin | Connector_PinHeader_2.54mm:PinHeader_1x04_P2.54mm_Vertical | ~ | 1
J3 | J4 | J5 | J6 | Conn_01x02_Pin | Connector_PinHeader_2.54mm:PinHeader_1x02_P2.54mm_Vertical | ~ | 4
J7 | Conn_01x03_Pin | Connector_PinHeader_2.54mm:PinHeader_1x03_P2.54mm_Vertical | ~ | 1
JP1 JP2 JP3 JP4 JP5 JP8 JP9 JP10 | SolderJumper_3_Open | Jumper:SolderJumper-3_P1.3mm_Open_RoundedPad1.0x1.5mm_NumberLabels | ~ | 8 |  | Excluded from BOM
JP6 JP7 | SolderJumper_3_Open | Jumper:SolderJumper-3_P1.3mm_Open_Pad1.0x1.5mm | ~ | 2 |  | Excluded from BOM
LEFT_LC_CONN1 | RIGHT_LC_CONN1 | CONN_04X2 | Connector_PinHeader_2.54mm:PinHeader_2x04_P2.54mm_Vertical |  | 2
PS1 | P78E05-1000 | TMotor_Rev0_5_1_Mark_2_NAU_OpenExo:P78E05-1000 |  | 1 |  |  |  | Discountinued
R1 R2 | 10R | Resistor_THT:R_Axial_DIN0207_L6.3mm_D2.5mm_P10.16mm_Horizontal |  | 2
R3 R4 R5 R6 | 4.7k | Resistor_THT:R_Axial_DIN0207_L6.3mm_D2.5mm_P10.16mm_Horizontal | ~ | 4
R11 R12 | 120R | Resistor_THT:R_Axial_DIN0207_L6.3mm_D2.5mm_P10.16mm_Horizontal |  | 2
R15 | R16 | R17 | R18 | 470R | Resistor_THT:R_Axial_DIN0207_L6.3mm_D2.5mm_P10.16mm_Horizontal |  | 4
SHUNT0 | 2mOhm | TMotor_Rev0_5_1_Mark_2_NAU_OpenExo:STA_CSNL2512(2)_STP |  | 1 |  |  |  | NOTE : unsolder from the PCB
U$6 | 0458002.DR | TMotor_Rev0_5_1_Mark_2_NAU_OpenExo:FUSE_LITTEL_448 |  | 1
U1 | TXU0104PWR | TXU0104:SOIC_QPWRQ1_TEX |  | 1
U2 | TXU0304-Q1 | TXU0304:PW14_TXU0304-Q1_TEX | TXU0304-Q1 | 1 |  |  |  | I ordered a different package
U3 U4 U6 U7 | INA125U | TMotor_Rev0_5_1_Mark_2_NAU_OpenExo:D16 |  | 4
U5 | SN65HVD230DR | TMotor_Rev0_5_1_Mark_2_NAU_OpenExo:SOIC127P599X175-8N |  | 1
U10 | DEV-16771 | TMotor_Rev0_5_1_Mark_2_NAU_OpenExo:MODULE_DEV-16771 |  | 1
USB0 | ABX00028 | TMotor_Rev0_5_1_Mark_2_NAU_OpenExo:ABX00028 |  | 1
XT30UPB-F2 XT30UPB-F4 XT30UPB-F5 XT30UPB-F6 XT30UPB-F7 | L_0 | TMotor_Rev0_5_1_Mark_2_NAU_OpenExo:XT30UPB-F |  | 5
CART ORDER LINK : https://www.digikey.ca/ordering/shoppingcart

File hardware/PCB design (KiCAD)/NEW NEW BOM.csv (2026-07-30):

Id | Designator | Footprint | Quantity | Designation | Supplier and ref
1 | U10 | SOT_32AIDDFR_TEX | 1 | INA232AIDDFR
2 | C44 | C_0805_2012Metric_Pad1.18x1.45mm_HandSolder | 1 | 10uF
3 | C43,C22,C6,C17,C4,C7,C2,C1,C3 | C_0805_2012Metric_Pad1.18x1.45mm_HandSolder | 9 | 0.1uF
4 | R30,R29 | R_0805_2012Metric_Pad1.20x1.40mm_HandSolder | 2 | 10k
5 | C24,C26,C29,C19,C23,C12,C28,C13,C31,C21,C16,C18,C5,C14 | C_0805_2012Metric_Pad1.18x1.45mm_HandSolder | 14 | 100nF
6 | C38,C37,C33,C40,C34,C32,C35,C27,C39,C36 | C_0805_2012Metric_Pad1.18x1.45mm_HandSolder | 10 | 10nF
7 | RIGHT_LC_CONN1,LEFT_LC_CONN1,RIGHT_LC_CONN2 | SAMTEC_TFM-107-01-L-D-WT | 3 | TFM-107-01-L-D-WT
8 | CAN_L1,CAN_R1 | MOLEX_5015680207 | 2 | 5015680207
9 | D1 | D_DO-201AD_P15.24mm_Horizontal | 1 | 1N5400
10 | U7 | MODULE_DEV-16771 | 1 | DEV-16771
11 | R4,R1 | R_0805_2012Metric_Pad1.20x1.40mm_HandSolder | 2 | 120R
12 | R21,R16,R13,R17,R20,R8,R9,R12 | R_0805_2012Metric_Pad1.20x1.40mm_HandSolder | 8 | 100k
13 | C8 | CP_Radial_D10.0mm_P5.00mm | 1 | C_Polarized_US
14 | J4,J3,J5 | PinHeader_1x02_P2.54mm_Vertical | 3 | Conn_01x02_Pin
15 | A1 | Arduino_Nano_Every_Socket | 1 | Arduino_Nano_33_BLE_Sense_R2_Socket
16 | J2 | PinHeader_1x04_P2.54mm_Vertical | 1 | Conn_01x04_Pin
17 | D10,D8,D9,D7 | P200_SOT-23 | 4 | BAS70-04
18 | SHUNT1 | STA_CSNL2512(2)_STP | 1 | 2mOhm
19 | TP2,TP1 | TestPoint_Keystone_5000-5004_Miniature | 2 | TestPoint
20 | R26 | R_0805_2012Metric_Pad1.20x1.40mm_HandSolder | 1 | 470
21 | U9 | WPME-FDSM_17301XX35 | 1 | WPME-FDSM_SIP-3
22 | R23,R5,R6,R14,R18,R10,R25,R31,R22,R24,R32 | R_0805_2012Metric_Pad1.20x1.40mm_HandSolder | 11 | 1k
23 | J9,J11,J10,J8,J7 | AMASS_XT30U-F_1x02_P5.0mm_Vertical | 5 | XT30PW-F
24 | J1 | PinHeader_2x03_P2.54mm_Vertical | 1 | Conn_02x03_Counter_Clockwise
25 | D3,D2 | LED_0805_2012Metric | 2 | LED
26 | C15,C25,C30,C20 | C_0805_2012Metric_Pad1.18x1.45mm_HandSolder | 4 | 1uF
27 | U$1 | FUSE_LITTEL_448 | 1 | 0458002.DR
28 | R3,R2 | R_0805_2012Metric_Pad1.20x1.40mm_HandSolder | 2 | 10
29 | R11,R15,R7,R19 | R_0805_2012Metric_Pad1.20x1.40mm_HandSolder | 4 | 50
30 | C10,C11 | C_0805_2012Metric_Pad1.18x1.45mm_HandSolder | 2 | 22uF
31 | U2,U4,U1,U3 | D16 | 4 | INA125U
32 | R27,R28 | R_0805_2012Metric_Pad1.20x1.40mm_HandSolder | 2 | 3.3k
33 | U5 | SOIC_QPWRQ1_TEX | 1 | TXU0104PWR
34 | C9 | C_0805_2012Metric_Pad1.18x1.45mm_HandSolder | 1 | 0.33uF
35 | U8 | SOIC127P599X175-8N | 1 | SN65HVD230DR
36 | U6 | PW14_TXU0304-Q1_TEX | 1 | TXU0304-Q1

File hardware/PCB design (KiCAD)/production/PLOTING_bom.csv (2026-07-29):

Designator | Footprint | Quantity | Value | LCSC Part #
A1 | Arduino_Nano_Every_Socket | 1 | Arduino_Nano_33_BLE_Sense_R2_Socket
C1, C17, C2, C22, C3, C4, C6, C7 | 0805 | 8 | 0.1uF
C10, C11 | 0805 | 2 | 22uF
C12, C13, C14, C16, C18, C19, C21, C23, C24, C26, C28, C29, C31, C5 | 0805 | 14 | 100nF
C15, C20, C25, C30 | 0805 | 4 | 1uF
C27, C32, C33, C34, C35, C36, C37, C38, C39, C40 | 0805 | 10 | 10nF
C8 | CP_Radial_D10.0mm_P5.00mm | 1 | C_Polarized_US
C9 | 0805 | 1 | 0.33uF
CAN_L1, CAN_R1 | MOLEX_5015680207 | 2 | 5015680207
D1 | D_DO-201AD_P15.24mm_Horizontal | 1 | 1N5400
D10, D7, D8, D9 | P200_SOT-23 | 4 | BAS70-04
D2, D3 | 0805 | 2 | LED
J10, J11, J7, J8, J9 | AMASS_XT30U-F_1x02_P5.0mm_Vertical | 5 | XT30PW-F
J2 | PinHeader_1x04_P2.54mm_Vertical | 1 | Conn_01x04_Pin
J3, J4, J5 | PinHeader_1x02_P2.54mm_Vertical | 3 | Conn_01x02_Pin
J6 | PinHeader_1x03_P2.54mm_Vertical | 1 | Conn_01x03_Pin
LEFT_LC_CONN1, RIGHT_LC_CONN1, RIGHT_LC_CONN2 | SAMTEC_TFM-107-01-L-D-WT | 3 | TFM-107-01-L-D-WT
R1, R4 | 0805 | 2 | 120R
R10, R14, R18, R22, R23, R24, R25, R31, R32, R5, R6 | 0805 | 11 | 1k
R11, R15, R19, R7 | 0805 | 4 | 50
R12, R13, R16, R17, R20, R21, R8, R9 | 0805 | 8 | 100k
R2, R3 | 0805 | 2 | 10
R26 | 0805 | 1 | 470
R27, R28 | 0805 | 2 | 3.3k
R29, R30 | R_Axial_DIN0207_L6.3mm_D2.5mm_P7.62mm_Horizontal | 2 | 10k
SHUNT1 | STA_CSNL2512(2)_STP | 1 | 2mOhm
TP1, TP2 | TestPoint_Keystone_5000-5004_Miniature | 2 | TestPoint
U$1 | FUSE_LITTEL_448 | 1 | 0458002.DR
U1, U2, U3, U4 | D16 | 4 | INA125U
U10 | SOT_32AIDDFR_TEX | 1 | INA232AIDDFR
U5 | SOIC_QPWRQ1_TEX | 1 | TXU0104PWR
U6 | PW14_TXU0304-Q1_TEX | 1 | TXU0304-Q1
U7 | MODULE_DEV-16771 | 1 | DEV-16771
U8 | SOIC127P599X175-8N | 1 | SN65HVD230DR
U9 | WPME-FDSM_17301XX35 | 1 | WPME-FDSM_SIP-3

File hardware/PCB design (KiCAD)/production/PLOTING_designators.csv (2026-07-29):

A1:1
C1:1
C10:1
C11:1
C12:1
C13:1
C14:1
C15:1
C16:1
C17:1
C18:1
C19:1
C2:1
C20:1
C21:1
C22:1
C23:1
C24:1
C25:1
C26:1
C27:1
C28:1
C29:1
C3:1
C30:1
C31:1
C32:1
C33:1
C34:1
C35:1
C36:1
C37:1
C38:1
C39:1
C4:1
C40:1
C5:1
C6:1
C7:1
C8:1
C9:1
CAN_L1:1
CAN_R1:1
D1:1
D10:1
D2:1
D3:1
D7:1
D8:1
D9:1
G***:1
INA_EXC_JP1:1
INA_EXC_JP2:1
INA_EXC_JP3:1
INA_EXC_JP4:1
J10:1
J11:1
J2:1
J3:1
J4:1
J5:1
J6:1
J7:1
J8:1
J9:1
JP1:1
JP2:1
LEFT_LC_CONN1:1
NT1:1
R1:1
R10:1
R11:1
R12:1
R13:1
R14:1
R15:1
R16:1
R17:1
R18:1
R19:1
R2:1
R20:1
R21:1
R22:1
R23:1
R24:1
R25:1
R26:1
R27:1
R28:1
R29:1
R3:1
R30:1
R31:1
R32:1
R4:1
R5:1
R6:1
R7:1
R8:1
R9:1
RIGHT_LC_CONN1:1
RIGHT_LC_CONN2:1
SHUNT1:1
TEENSYPOWERJP1:1
TP1:1
TP2:1
U$1:1
U1:1
U10:1
U2:1
U3:1
U4:1
U5:1
U6:1
U7:1
U8:1
U9:1

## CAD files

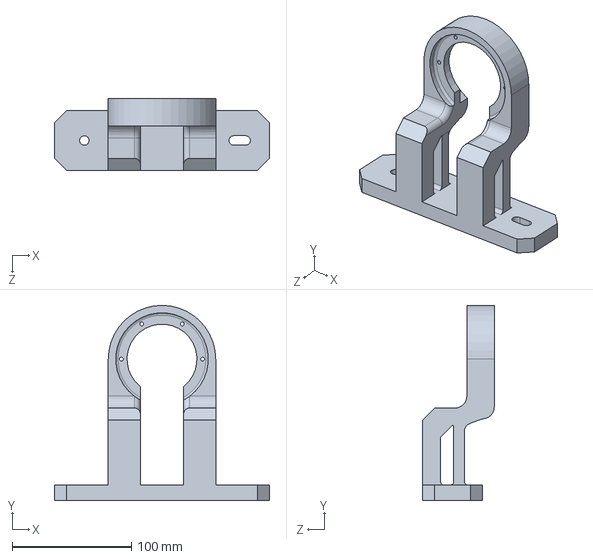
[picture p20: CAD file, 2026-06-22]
docs/user/mechanical/CAD-files/motor-mount.SLDPRT
180.0 x 163.5 x 60.0 mm

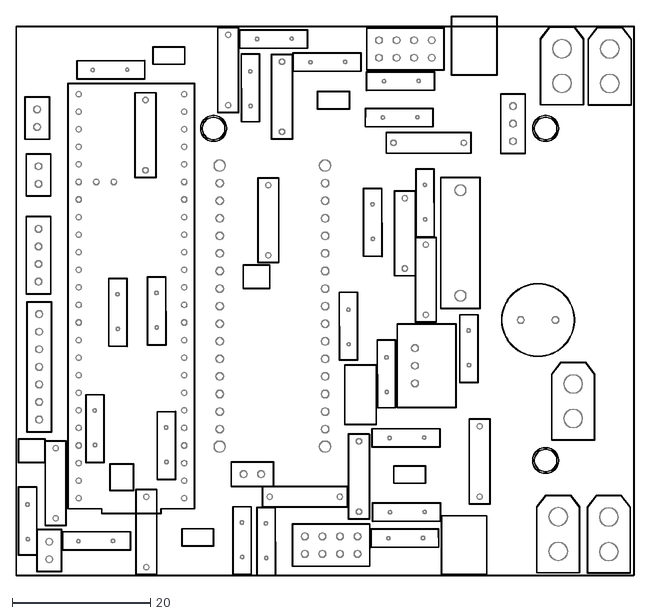
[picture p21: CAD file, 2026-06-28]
hardware/PCB design (KiCAD)/TMotor_Rev0_5_1_Mark_2_NAU_OpenExo-Edge_Cuts.dxf
89.3 x 80.8

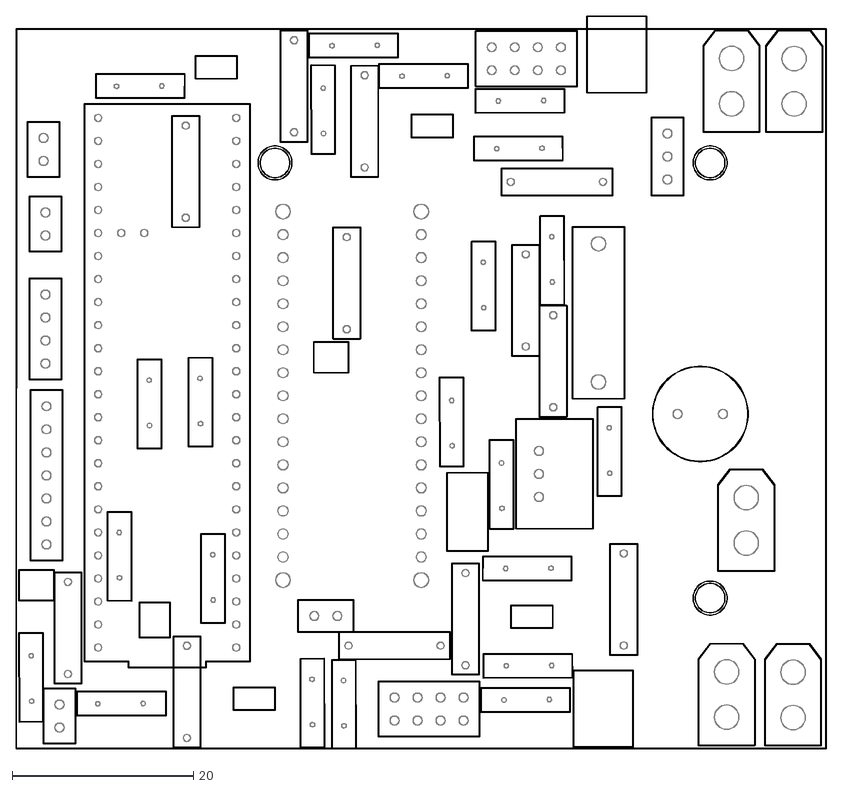
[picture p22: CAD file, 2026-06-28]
hardware/PCB design (KiCAD)/TMotor_Rev0_5_1_Mark_2_NAU_OpenExo-F_Courtyard.dxf
89.3 x 80.8

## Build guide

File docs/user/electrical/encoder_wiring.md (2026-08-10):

As explained in [the software/encoder page](/old%20software/encoder), the two encoders will share one SPI bus

The wiring of the two AMT-14C-0-036-1 cables to the main board was done as follows :

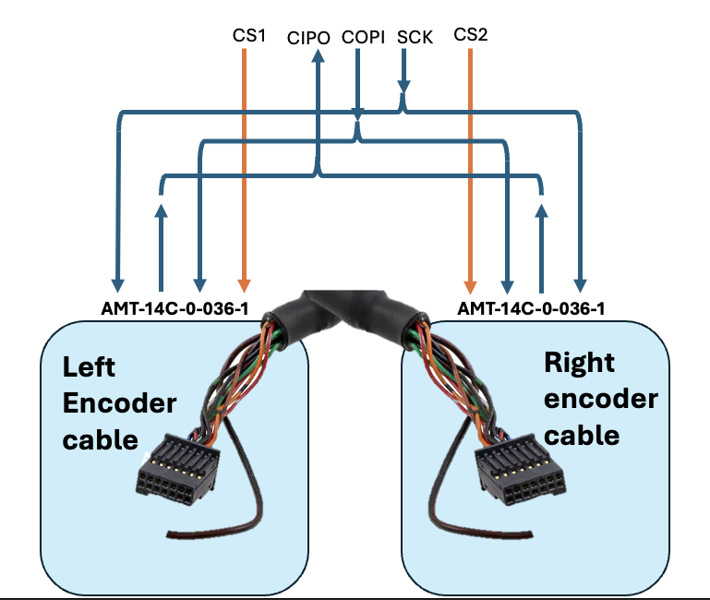
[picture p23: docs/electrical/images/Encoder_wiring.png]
wiring of encoder cables


The two cables merge together and on the other side is a 1x7 2.54mm female jumper header which will be connected on the PCB at the location specified with the label `SPIx2`

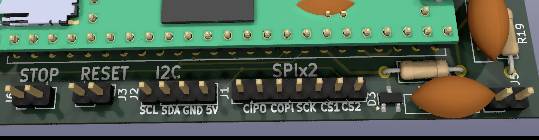
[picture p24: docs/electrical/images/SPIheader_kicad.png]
KiCAD rendering of SPI header


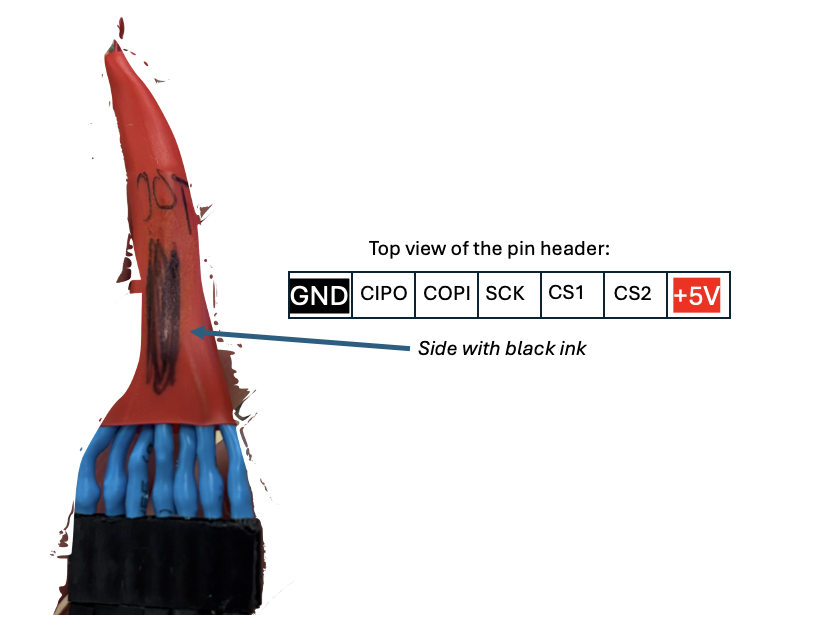
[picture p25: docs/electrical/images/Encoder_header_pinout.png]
Pinout of the female header


Note that the side with black ink on the red heatshrink should be put on the out-side of the board i.e face back from the PCB

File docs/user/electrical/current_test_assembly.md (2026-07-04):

## IMPORTANT notes for using the current setup for the Exo testbench

The setup looks like this from the top : 

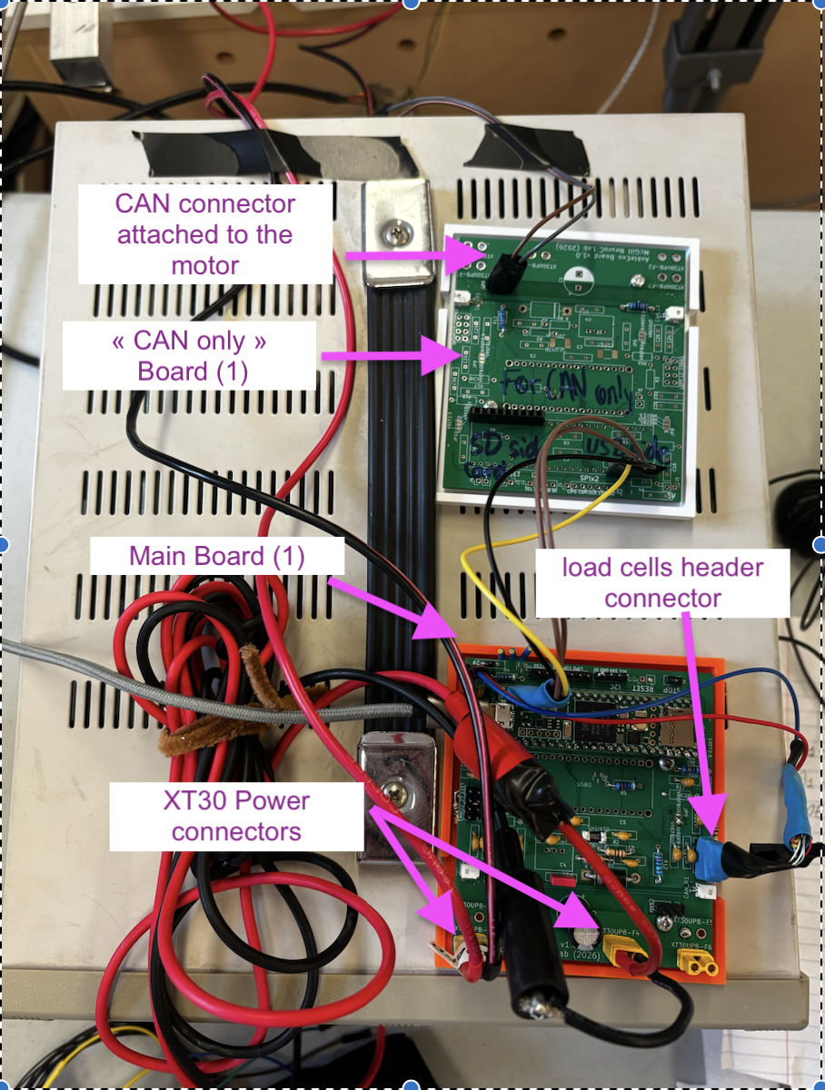
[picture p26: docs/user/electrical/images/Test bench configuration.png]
Image of the boards for test bench


The main components in the configuration are :

1. The _Main_ board with most of the components soldered on (screwed onto the orange socket). It handles :
    - hardware interface and circuitry to/from the teensy
    - load cell amplification _for the two load cells currently mounted on the test bench_ (for more information about the connections for that header refer to [the load cell header pinout page](/electrical/pcb))

* The header must be put in such a way that the "OUT" inscription in dark ink appears on the outside of the board edge (see picture below)
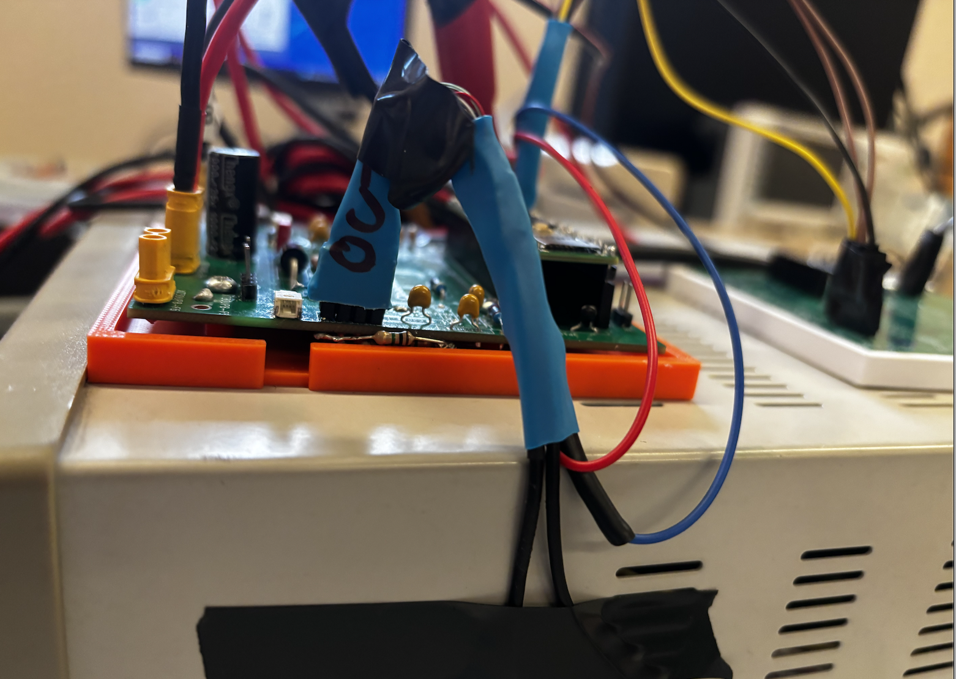
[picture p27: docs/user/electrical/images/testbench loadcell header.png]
load cell encoder


2. The _Secondary_ and temporary "CAN only board" in the white socket. Because I ran into a hardware issue with trying to make the CAN chip work on the main PCB, I temporarily used another separate PCB that will exclusively handle CAN.
   - The Teensy being on the _Main_ board, I also had to solder on-the-fly cables to interface the CAN chip on the remote board. _Please do not disconnect them_

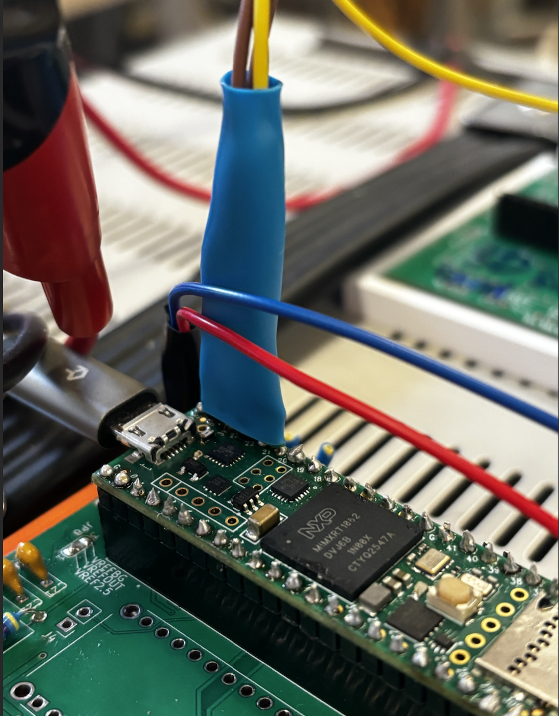
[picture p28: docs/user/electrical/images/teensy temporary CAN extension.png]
temporary soldered cables for powering remote CAN board

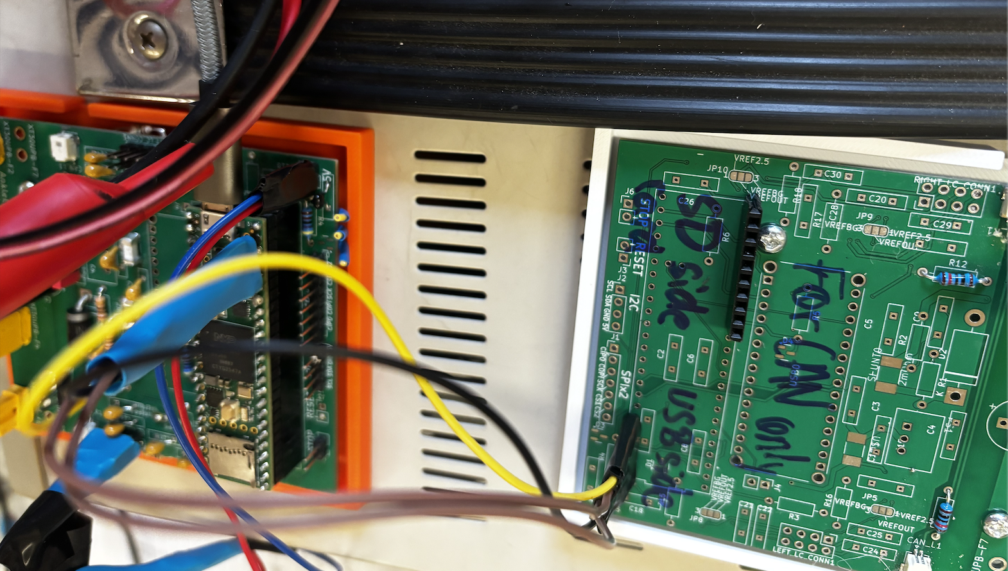
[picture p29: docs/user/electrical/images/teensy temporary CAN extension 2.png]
temporary soldered cables for powering remote CAN board


Side note for SPI : 
* The current PCB version (rev. 1.0.0) _DOES NOT_ support using SPI through the Teensy, as I realized after ordering the boards that the connections were mismatched for the level shifters raising / lowering 3.3V / 5V to/from the Teensy and the Encoders.

As such you must use the Arduino Uno R3 or R4 in order to read the encoder value over SPI. The Teensy won't work.

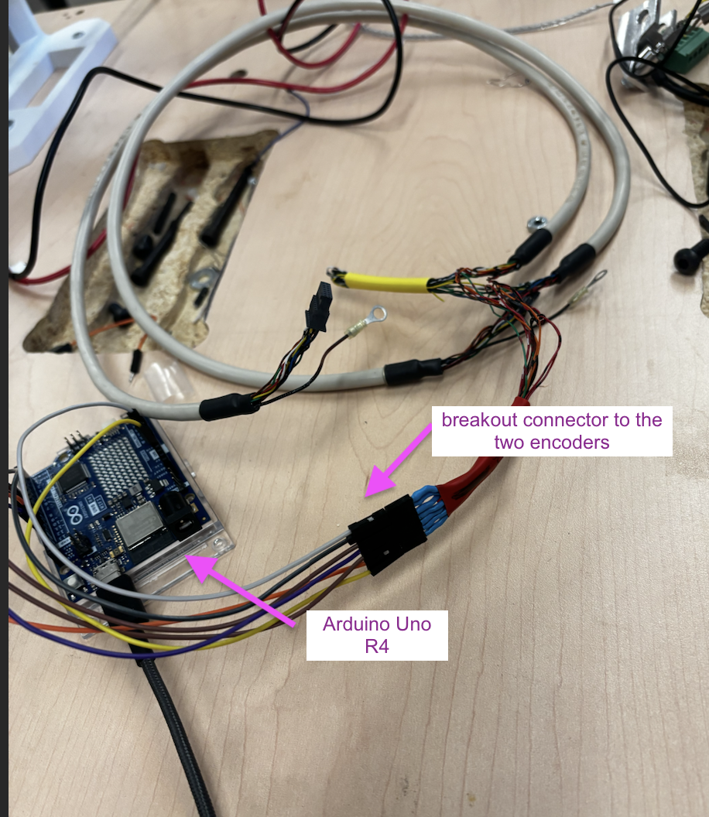
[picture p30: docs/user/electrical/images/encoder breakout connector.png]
Arduino Uno SPI setup for dual encoder reading


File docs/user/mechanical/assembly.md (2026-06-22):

## Updated Ankle Exoskeleton Assembly

The updated ankle exoskeleton mechanical design can be found in the Siemens NX assembly called "Ankle_Exoskeleton_ASM" (TO VERIFY)

Download ZIP: [Ankle Exoskeleton Assembly](../CAD-files/ankle-exo.zip)

** Note that some part files may have non fully defined sketches

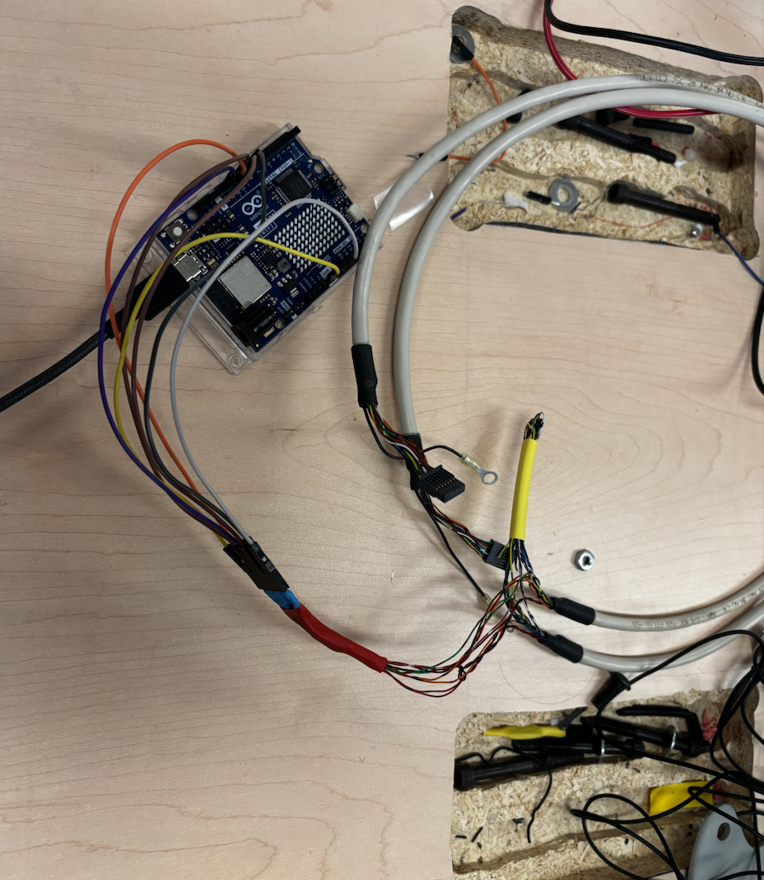
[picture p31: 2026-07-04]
docs/user/electrical/images/Arduino Uno R4 encoder setup.png

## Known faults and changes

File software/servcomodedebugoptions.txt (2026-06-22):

Valid commands are:
help
  Show this help
ping
  Print pong here to see if the reply works
stop
  Stop the motor
last_adc_duration
  The time the latest ADC interrupt consumed
kv
  The calculated kv of the motor
mem
  Show memory usage
threads
  List all threads
fault
  Prints the current fault code
faults
  Prints all stored fault codes and conditions when they arrived
rpm
  Prints the current electrical RPM
tacho
  Prints tachometer value
tim
  Prints tim1 and tim8 settings
volt
  Prints different voltages
param_detect [current] [min_rpm] [low_duty]
  Spin up the motor in COMM_MODE_DELAY and compute its parameters.
  This test should be performed without load on the motor.
  Example: param_detect 5.0 600 0.06
rpm_dep
  Prints some rpm-dep values
can_devs
  Prints all CAN devices seen on the bus the past second
foc_encoder_detect [current]
  Run the motor at 1Hz on open loop and compute encoder settings
measure_res [current]
  Lock the motor with a current and calculate its resistance
measure_ind [duty]
  Send short voltage pulses, measure the current and calculate the motor inductance
measure_linkage [current] [duty] [min_erpm] [motor_res]
  Run the motor in BLDC delay mode and measure the flux linkage
  example measure_linkage 5 0.5 700 0.076
  tip: measure the resistance with measure_res first
measure_res_ind
  Measure the motor resistance and inductance with an incremental adaptive algorithm.
measure_linkage_foc [duty]
  Run the motor with FOC and measure the flux linkage.
measure_linkage_openloop [current] [duty] [erpm_per_sec] [motor_res] [motor_ind]
  Run the motor in openloop FOC and measure the flux linkage
  example measure_linkage 5 0.5 1000 0.076 0.000015
  tip: measure the resistance with measure_res first
foc_state
  Print some FOC state variables.
hw_status
  Print some hardware status information.
foc_openloop [current] [erpm]
  Create an open loop rotating current vector.
foc_openloop_duty [duty] [erpm]
  Create an open loop rotating voltage vector.
nrf_ext_set_enabled [enabled]
  Enable or disable external NRF51822.
foc_sensors_detect_apply [current]
  Automatically detect FOC sensors, and apply settings on success.
rotor_lock_openloop [current_A] [time_S] [angle_DEG]
  Lock the motor with a current for a given time. Time 0 means forever, or
  or until the heartbeat packets stop.
foc_detect_apply_all [max_power_loss_W]
  Detect and apply all motor settings, based on maximum resistive motor power losses.
can_scan
  Scan CAN-bus using ping commands, and print all devices that are found.
foc_detect_apply_all_can [max_power_loss_W]
  Detect and apply all motor settings, based on maximum resistive motor power losses. Also
  initiates detection in all VESCs found on the CAN-bus.
encoder
  Prints the status of the AS5047, AD2S1205, or TS5700N8501 encoder.
encoder_clear_errors
  Clear error of the TS5700N8501 encoder.)
encoder_clear_multiturn
  Clear multiturn counter of the TS5700N8501 encoder.)
uptime
  Prints how many seconds have passed since boot.
hall_analyze [current]
  Rotate motor in open loop and analyze hall sensors.
Calibrate_outenc
  Calibrate the motor external encoder.
Accuracy_test
  Verify the results of calibrating the external encoder.
zhunquedu [error accuracy]
  Set error accuracy.
connect_virtual_motor [ml][J][Ld][Lq][Rs][lambda][Vbus]
  connects virtual motor
disconnect_virtual_motor
  disconnect virtual motor
foc_plot_hfi_en [en]
  Enable HFI plotting. 0: off, 1: DFT, 2: Raw
uavcan_debug [level]
  Enable UAVCAN debug prints (0 = off)
nunchuk_status
  Print the status of the nunchuk app
bm_swdp_scan
  BlackMagic: Scan SWD
bm_attach [index]
  BlackMagic: Attach target
bm_flash_erase [hex_addr] [len]
  BlackMagic: Erase flash memory
bm_target_help
  BlackMagic: Show target commands
bm_target_cmd [...]
  BlackMagic: Run command on target
bm_detach
  BlackMagic: Detach target

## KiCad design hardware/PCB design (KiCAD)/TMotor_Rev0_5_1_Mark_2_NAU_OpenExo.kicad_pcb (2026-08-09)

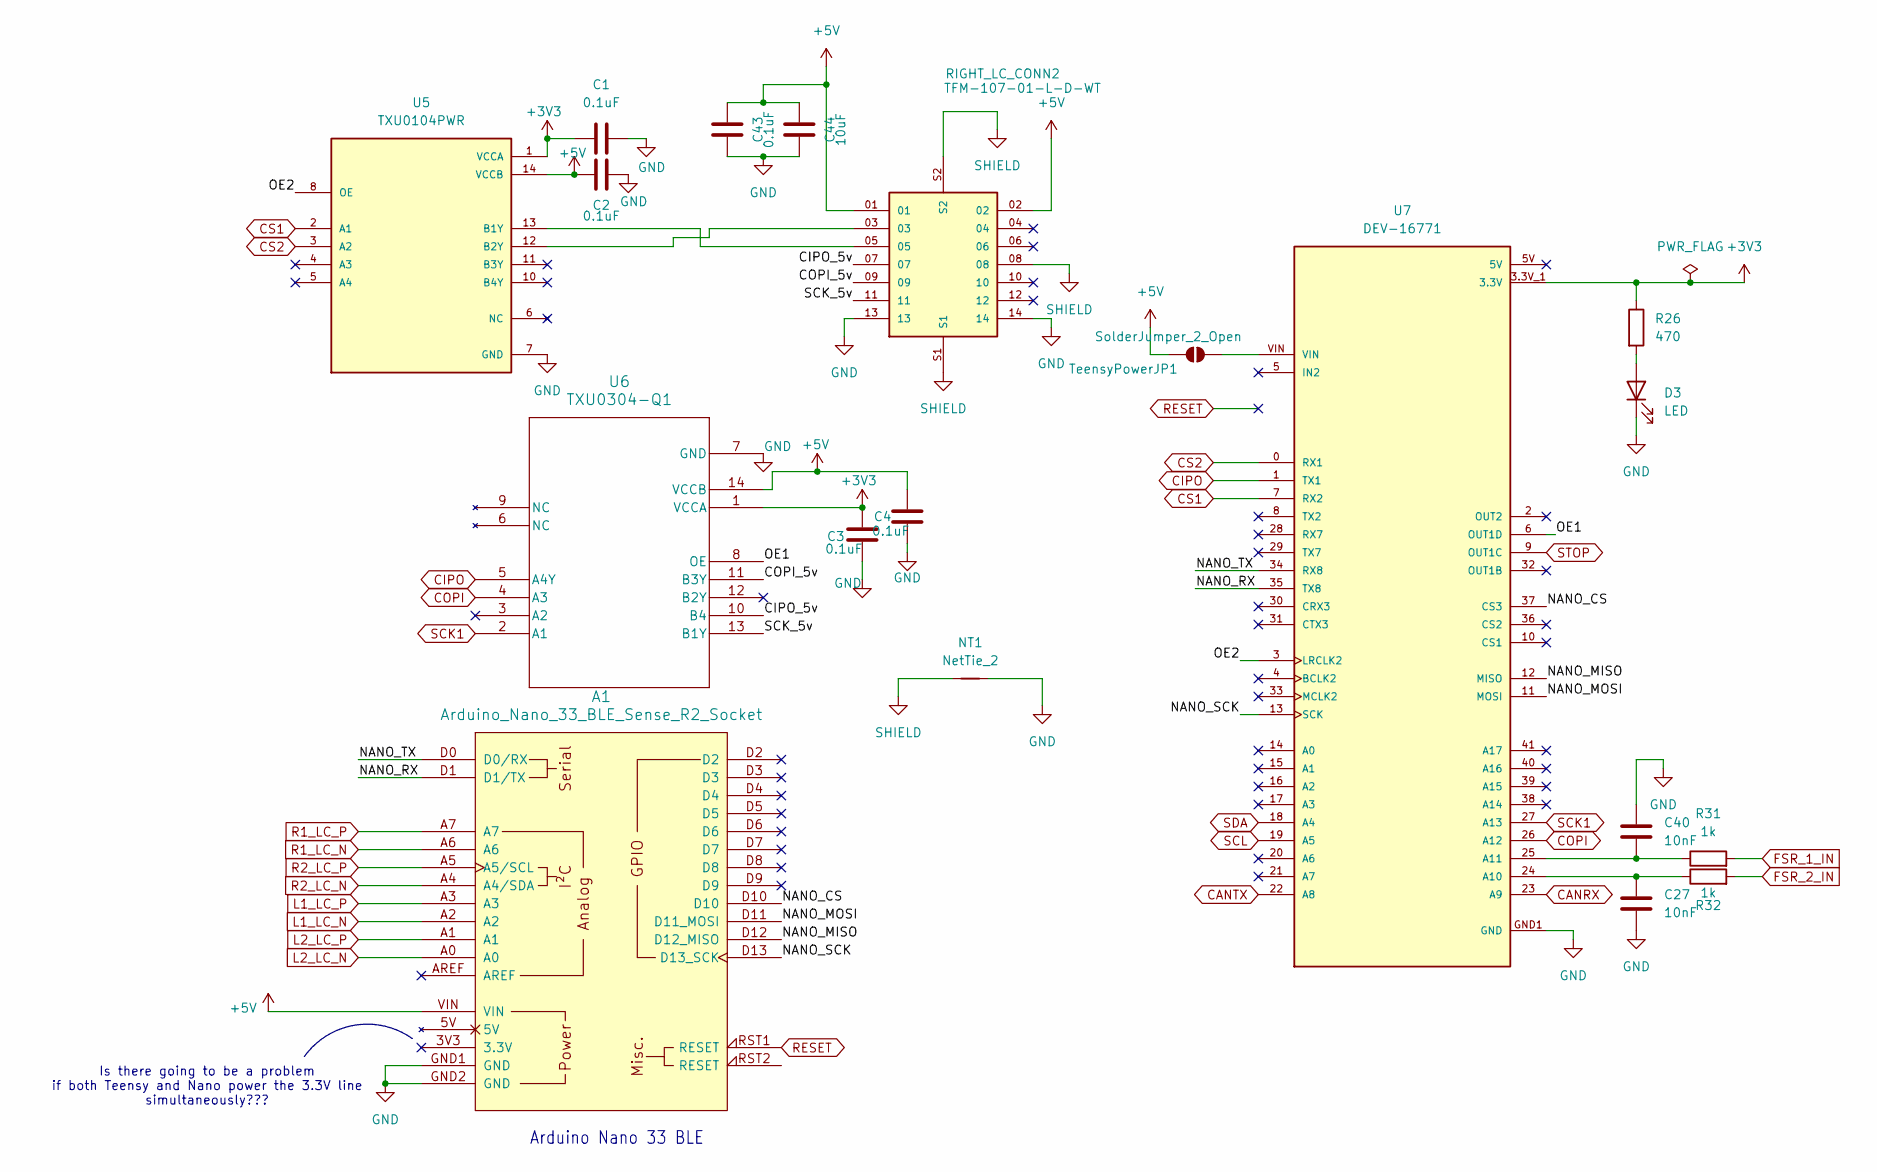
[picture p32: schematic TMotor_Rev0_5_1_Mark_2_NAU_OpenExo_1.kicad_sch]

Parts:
A1: Arduino_Nano_33_BLE_Sense_R2_Socket; Arduino_Nano_Every_Socket
C1, C2, C3, C4, C43: 0.1uF; C_0805_2012Metric_Pad1.18x1.45mm_HandSolder
C27, C40: 10nF; C_0805_2012Metric_Pad1.18x1.45mm_HandSolder
C44: 10uF; C_0805_2012Metric_Pad1.18x1.45mm_HandSolder
D3: LED; LED_0805_2012Metric
NT1: NetTie_2; NetTie-2_SMD_Pad0.5mm
R26: 470; R_0805_2012Metric_Pad1.20x1.40mm_HandSolder
R31, R32: 1k; R_0805_2012Metric_Pad1.20x1.40mm_HandSolder
RIGHT_LC_CONN2: TFM-107-01-L-D-WT; SAMTEC_TFM-107-01-L-D-WT; PARTREV T
TeensyPowerJP1: SolderJumper_2_Open; SolderJumper-2_P1.3mm_Open_RoundedPad1.0x1.5mm
U5: TXU0104PWR; SOIC_QPWRQ1_TEX; PARTREV A
U6: TXU0304-Q1; PW14_TXU0304-Q1_TEX
U7: DEV-16771; MODULE_DEV-16771; PARTREV 4.1

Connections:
+3V3: C1.1, C3.2, R26.1, U5.1 (VCCA), U6.1 (VCCA), U7.3.3V_1 (3.3V), U7.3.3V_2 (3.3V), U7.3.3V_3 (3.3V); also elsewhere on the board
+5V: A1.VIN, C2.1, C4.2, C43.2, C44.2, RIGHT_LC_CONN2.01, RIGHT_LC_CONN2.02, TeensyPowerJP1.2 (B), U5.14 (VCCB), U6.14 (VCCB); also elsewhere on the board
/MCUs/CIPO_5v: RIGHT_LC_CONN2.07, U6.10 (B4)
/MCUs/COPI_5v: RIGHT_LC_CONN2.09, U6.11 (B3Y)
/MCUs/NANO_CS: A1.D10, U7.37 (CS3)
/MCUs/NANO_MISO: A1.D12 (D12_MISO), U7.12 (MISO)
/MCUs/NANO_MOSI: A1.D11 (D11_MOSI), U7.11 (MOSI)
/MCUs/NANO_RX: A1.D1 (D1/TX), U7.35 (TX8)
/MCUs/NANO_SCK: A1.D13 (D13_SCK), U7.13 (SCK)
/MCUs/NANO_TX: A1.D0 (D0/RX), U7.34 (RX8)
/MCUs/OE1: U6.8 (OE), U7.6 (OUT1D)
/MCUs/OE2: U5.8 (OE), U7.3 (LRCLK2)
/MCUs/SCK_5v: RIGHT_LC_CONN2.11, U6.13 (B1Y)
CANRX: U7.23 (A9); also elsewhere on the board
CANTX: U7.22 (A8); also elsewhere on the board
CIPO: U6.5 (A4Y), U7.1 (TX1)
COPI: U6.4 (A3), U7.26 (A12)
CS1: U5.2 (A1), U7.7 (RX2)
CS2: U5.3 (A2), U7.0 (RX1)
FSR_1_IN: R31.2; also elsewhere on the board
FSR_2_IN: R32.2; also elsewhere on the board
GND: A1.GND1 (GND), A1.GND2 (GND), C1.2, C2.2, C3.1, C4.1, C27.2, C40.1, C43.1, C44.1, D3.1 (K), NT1.2, RIGHT_LC_CONN2.13, RIGHT_LC_CONN2.14, U5.7 (GND), U6.7 (GND), U7.GND1 (GND), U7.GND2 (GND), U7.GND3 (GND), U7.GND4 (GND), U7.GND5 (GND); also elsewhere on the board
L1_LC_N: A1.A2; also elsewhere on the board
L1_LC_P: A1.A3; also elsewhere on the board
L2_LC_N: A1.A0; also elsewhere on the board
L2_LC_P: A1.A1; also elsewhere on the board
unnamed: D3.2 (A), R26.2
unnamed: TeensyPowerJP1.1 (A), U7.VIN
unnamed: RIGHT_LC_CONN2.05, U5.13 (B1Y)
unnamed: RIGHT_LC_CONN2.03, U5.12 (B2Y)
unnamed: C27.1, R32.1, U7.24 (A10)
unnamed: C40.2, R31.1, U7.25 (A11)
R1_LC_N: A1.A6; also elsewhere on the board
R1_LC_P: A1.A7; also elsewhere on the board
R2_LC_N: A1.A4 (A4/SDA); also elsewhere on the board
R2_LC_P: A1.A5 (A5/SCL); also elsewhere on the board
RESET: A1.RST1 (RESET); also elsewhere on the board
SCK1: U6.2 (A1), U7.27 (A13)
SCL: U7.19 (A5); also elsewhere on the board
SDA: U7.18 (A4); also elsewhere on the board
SHIELD: NT1.1, RIGHT_LC_CONN2.08, RIGHT_LC_CONN2.S1, RIGHT_LC_CONN2.S2; also elsewhere on the board
STOP: U7.9 (OUT1C); also elsewhere on the board

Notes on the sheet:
Is there going to be a problem if both Teensy and Nano power the 3.3V line simultaneously???
Arduino Nano 33 BLE

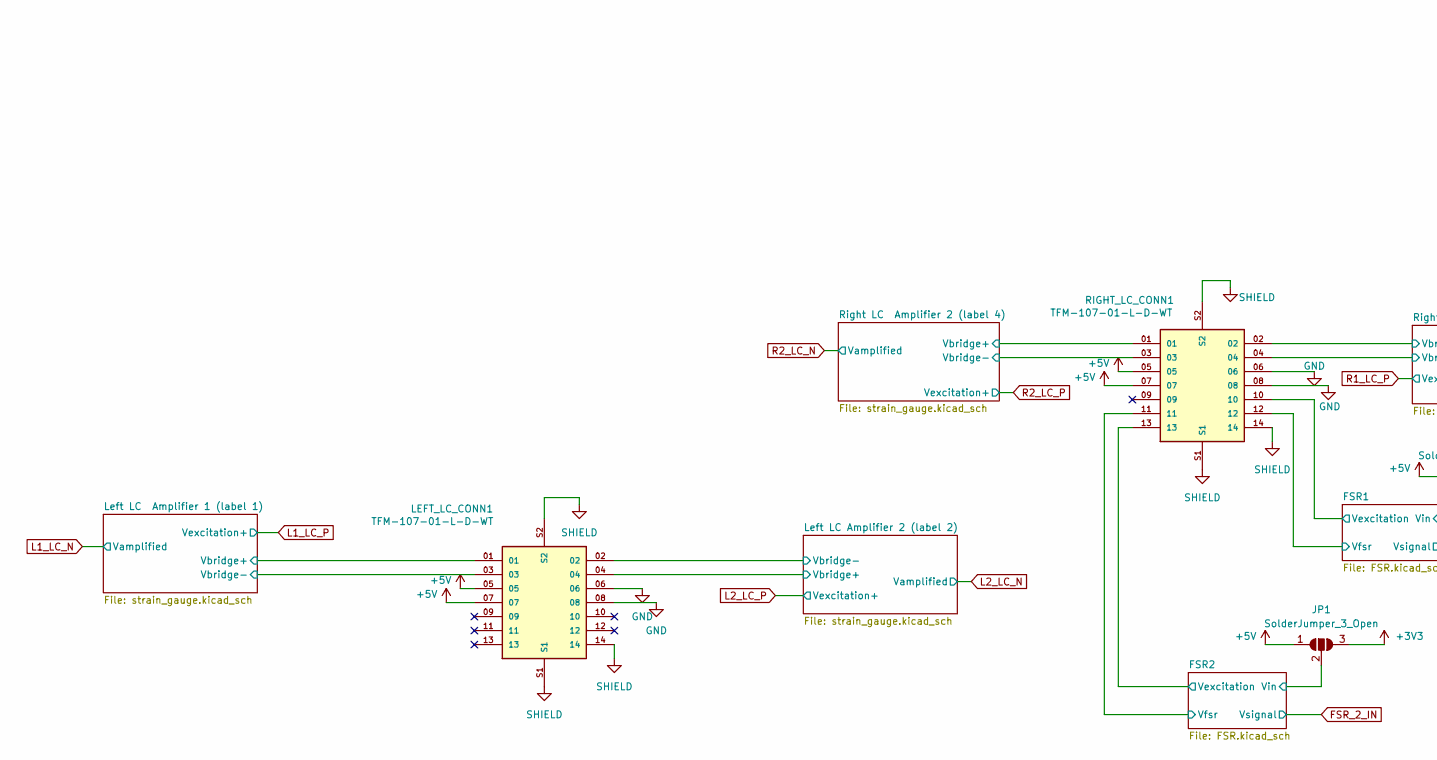
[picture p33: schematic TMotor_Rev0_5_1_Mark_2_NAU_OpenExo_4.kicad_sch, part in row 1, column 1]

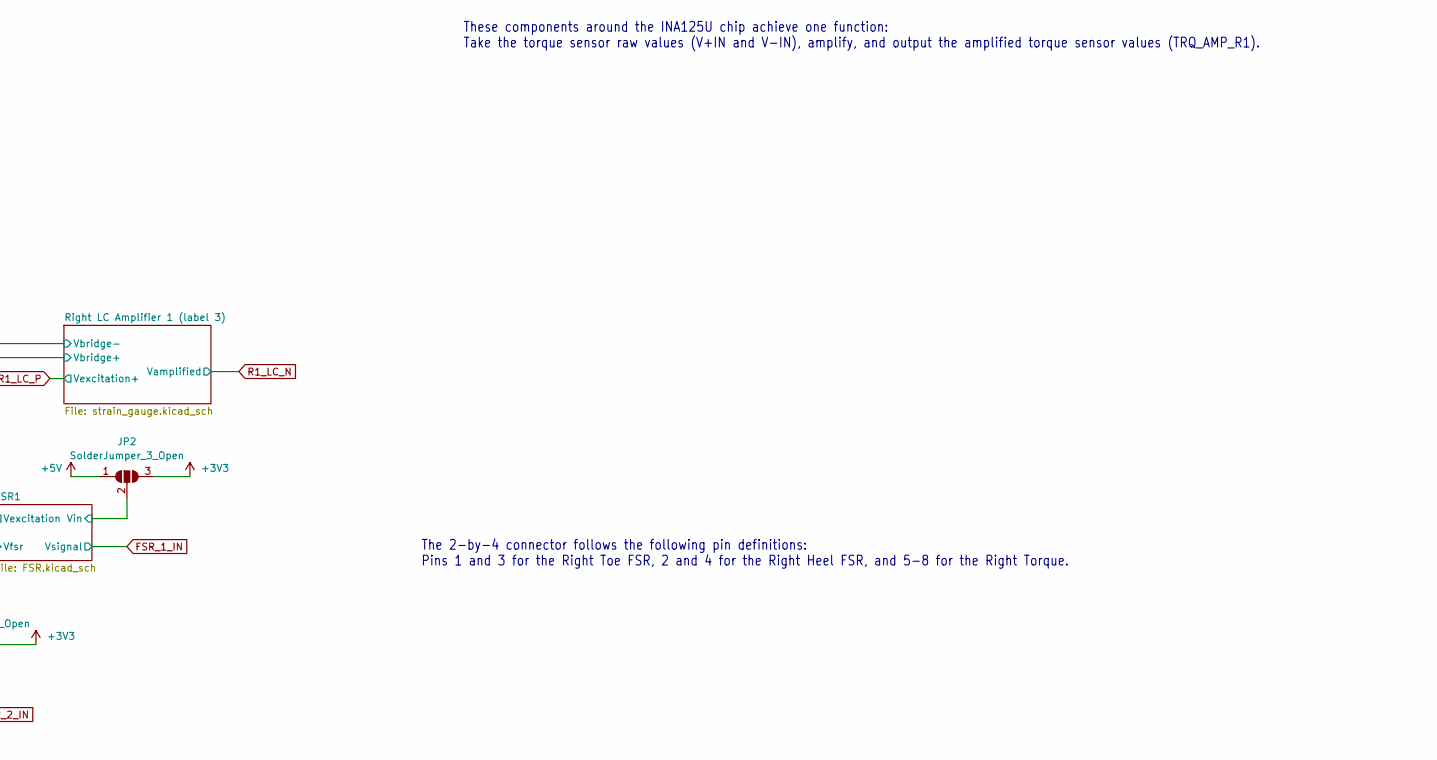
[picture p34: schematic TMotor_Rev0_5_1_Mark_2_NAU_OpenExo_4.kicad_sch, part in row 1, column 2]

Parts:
JP1, JP2: SolderJumper_3_Open; SolderJumper-3_P1.3mm_Open_RoundedPad1.0x1.5mm
LEFT_LC_CONN1: TFM-107-01-L-D-WT; SAMTEC_TFM-107-01-L-D-WT; PARTREV T
RIGHT_LC_CONN1: TFM-107-01-L-D-WT; SAMTEC_TFM-107-01-L-D-WT; PARTREV T

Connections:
+3V3: JP1.3 (B), JP2.3 (B); also elsewhere on the board
+5V: JP1.1 (A), JP2.1 (A), LEFT_LC_CONN1.05, LEFT_LC_CONN1.07, RIGHT_LC_CONN1.05, RIGHT_LC_CONN1.07; also elsewhere on the board
/Load cells/FSR1/Vexcitation: JP2.2 (C), RIGHT_LC_CONN1.10
/Load cells/FSR2/Vexcitation: JP1.2 (C), RIGHT_LC_CONN1.13
/Load cells/Left LC Amplifier 1 (label 1)/Vbridge+: LEFT_LC_CONN1.01; also elsewhere on the board
/Load cells/Left LC Amplifier 1 (label 1)/Vbridge-: LEFT_LC_CONN1.03; also elsewhere on the board
/Load cells/Left LC Amplifier 2 (label 2)/Vbridge+: LEFT_LC_CONN1.04; also elsewhere on the board
/Load cells/Left LC Amplifier 2 (label 2)/Vbridge-: LEFT_LC_CONN1.02; also elsewhere on the board
/Load cells/Right LC Amplifier 2 (label 4)/Vbridge+: RIGHT_LC_CONN1.01; also elsewhere on the board
/Load cells/Right LC Amplifier 2 (label 4)/Vbridge-: RIGHT_LC_CONN1.03; also elsewhere on the board
/Load cells/Right LC Amplifier 1 (label 3)/Vbridge+: RIGHT_LC_CONN1.04; also elsewhere on the board
/Load cells/Right LC Amplifier 1 (label 3)/Vbridge-: RIGHT_LC_CONN1.02; also elsewhere on the board
FSR_1_IN: RIGHT_LC_CONN1.12; also elsewhere on the board
FSR_2_IN: RIGHT_LC_CONN1.11; also elsewhere on the board
GND: LEFT_LC_CONN1.06, LEFT_LC_CONN1.08, RIGHT_LC_CONN1.06, RIGHT_LC_CONN1.08; also elsewhere on the board
SHIELD: LEFT_LC_CONN1.14, LEFT_LC_CONN1.S1, LEFT_LC_CONN1.S2, RIGHT_LC_CONN1.14, RIGHT_LC_CONN1.S1, RIGHT_LC_CONN1.S2; also elsewhere on the board

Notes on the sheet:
The 2-by-4 connector follows the following pin definitions: Pins 1 and 3 for the Right Toe FSR, 2 and 4 for the Right Heel FSR, and 5-8 for the Right Torque.
These components around the INA125U chip achieve one function: Take the torque sensor raw values (V+IN and V-IN), amplify, and output the amplified torque sensor values (TRQ_AMP_R1).

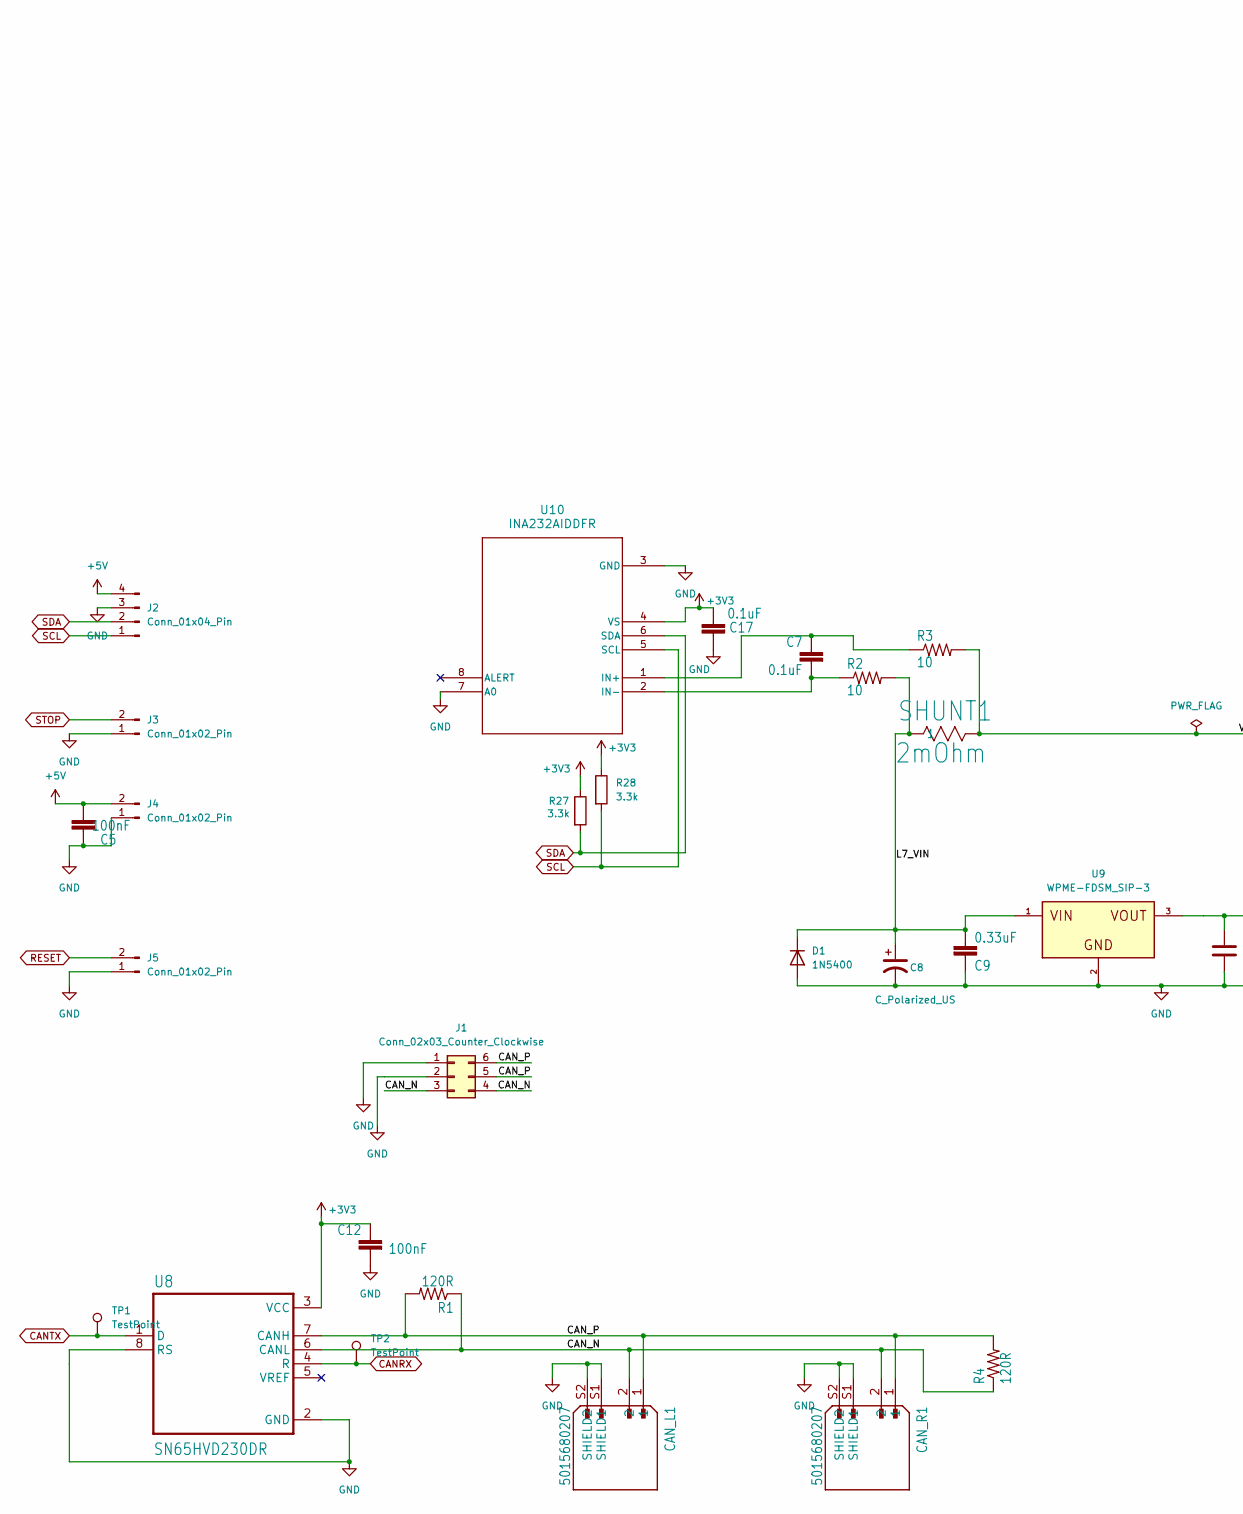
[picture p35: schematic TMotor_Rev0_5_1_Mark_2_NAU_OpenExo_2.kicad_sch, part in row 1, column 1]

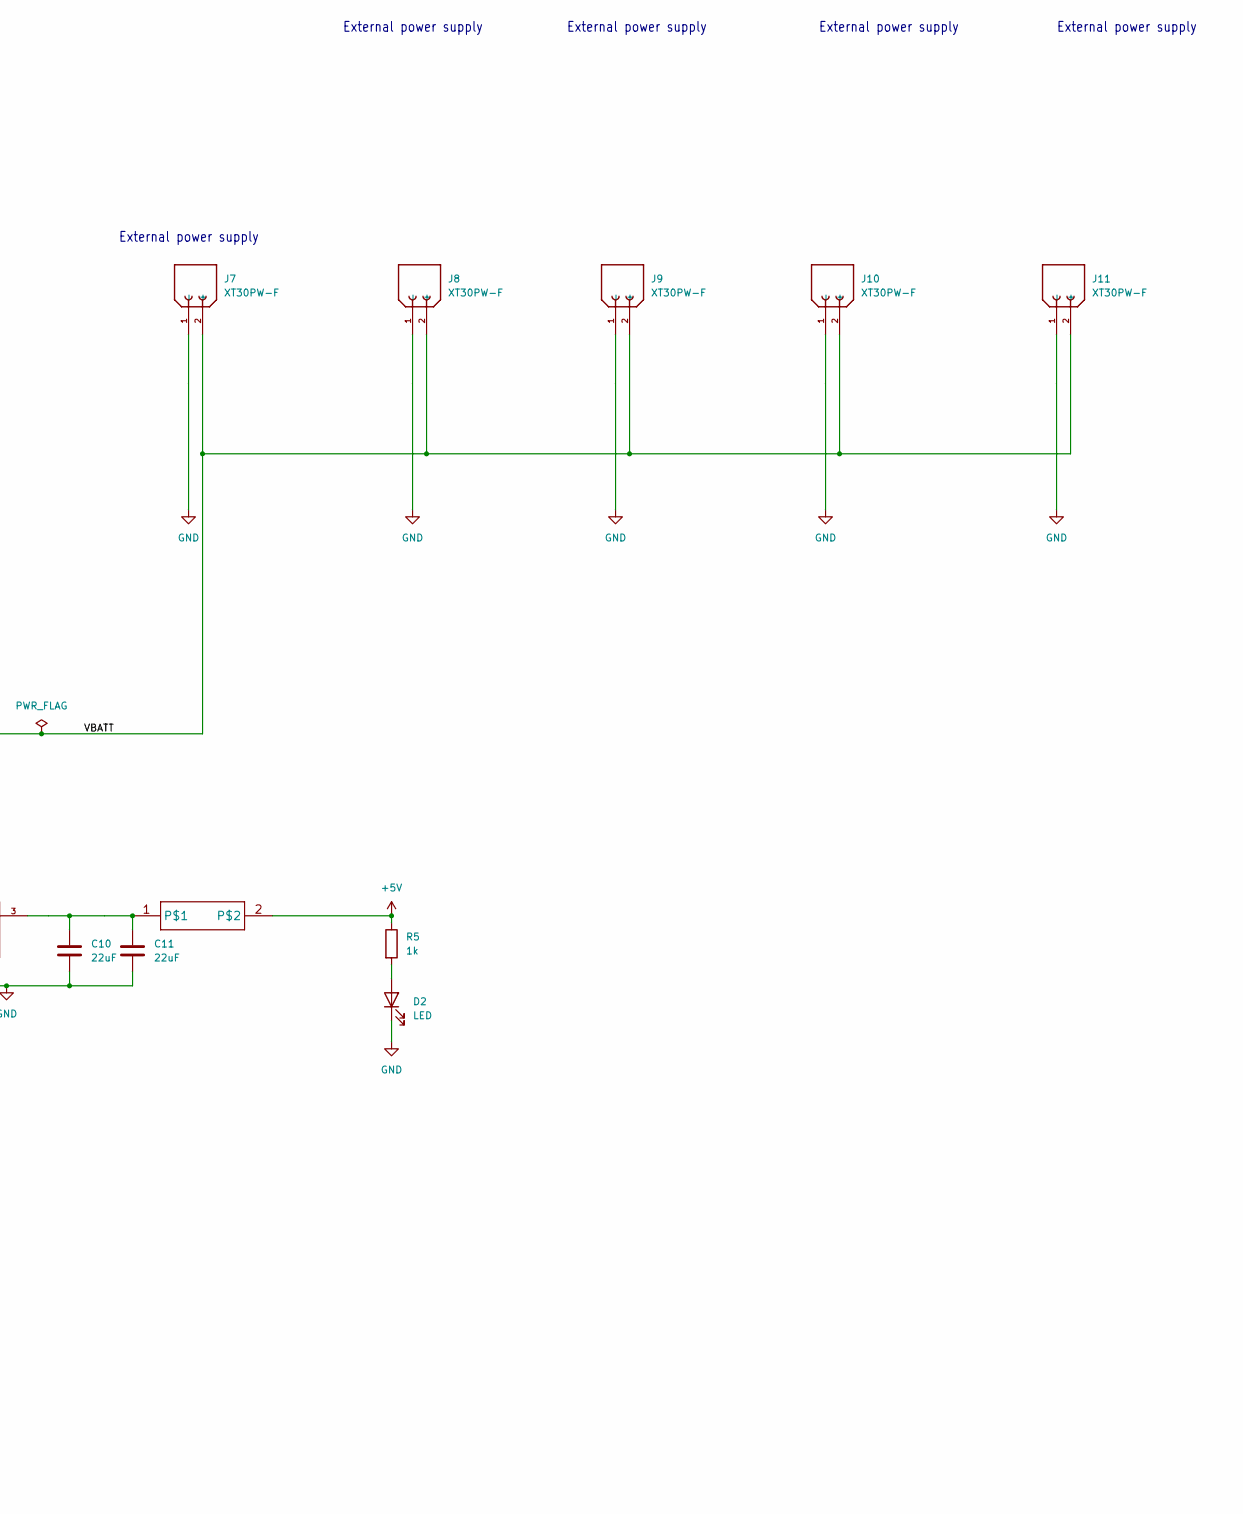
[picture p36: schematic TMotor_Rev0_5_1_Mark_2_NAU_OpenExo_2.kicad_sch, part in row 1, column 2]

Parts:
C5, C12: 100nF; C_0805_2012Metric_Pad1.18x1.45mm_HandSolder
C7, C17: 0.1uF; C_0805_2012Metric_Pad1.18x1.45mm_HandSolder
C8: C_Polarized_US; CP_Radial_D10.0mm_P5.00mm
C9: 0.33uF; C_0805_2012Metric_Pad1.18x1.45mm_HandSolder
C10, C11: 22uF; C_0805_2012Metric_Pad1.18x1.45mm_HandSolder
CAN_L1: 5015680207; MOLEX_5015680207
CAN_R1: 5015680207; MOLEX_5015680207
D1: 1N5400; D_DO-201AD_P15.24mm_Horizontal
D2: LED; LED_0805_2012Metric
J1: Conn_02x03_Counter_Clockwise; PinHeader_2x03_P2.54mm_Vertical
J2: Conn_01x04_Pin; PinHeader_1x04_P2.54mm_Vertical
J3, J4, J5: Conn_01x02_Pin; PinHeader_1x02_P2.54mm_Vertical
J7, J8, J9, J10, J11: XT30PW-F; AMASS_XT30U-F_1x02_P5.0mm_Vertical; PARTREV 1.2
R1, R4: 120R; R_0805_2012Metric_Pad1.20x1.40mm_HandSolder
R2, R3: 10; R_0805_2012Metric_Pad1.20x1.40mm_HandSolder
R5: 1k; R_0805_2012Metric_Pad1.20x1.40mm_HandSolder
R27, R28: 3.3k; R_0805_2012Metric_Pad1.20x1.40mm_HandSolder
SHUNT1: 2mOhm; STA_CSNL2512(2)_STP
TP1, TP2: TestPoint; TestPoint_Keystone_5000-5004_Miniature
U8: SN65HVD230DR; SOIC127P599X175-8N
U9: WPME-FDSM_SIP-3; WPME-FDSM_17301XX35; DigiKey_Part_Number 732-173010535-ND
U10: INA232AIDDFR; SOT_32AIDDFR_TEX
U$1: 0458002.DR; FUSE_LITTEL_448

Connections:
+3V3: C12.1, C17.2, R27.1, R28.1, U8.3 (VCC), U10.4 (VS); also elsewhere on the board
+5V: C5.2, J2.4, J4.2, R5.1, U$1.2; also elsewhere on the board
/CAN and peripherals./CAN_N: CAN_L1.2, CAN_R1.2, J1.3, J1.4, R1.1, R4.1, U8.6 (CANL)
/CAN and peripherals./CAN_P: CAN_L1.1, CAN_R1.1, J1.5, J1.6, R1.2, R4.2, U8.7 (CANH)
/CAN and peripherals./L7_VIN: C8.1, C9.2, D1.1 (K), R2.2, SHUNT1.1, U9.1
/CAN and peripherals./VBATT: J7.2 (+), J8.2 (+), J9.2 (+), J10.2 (+), J11.2 (+), R3.2, SHUNT1.2
CANRX: TP2.1, U8.4 (R); also elsewhere on the board
CANTX: TP1.1, U8.1 (D); also elsewhere on the board
GND: C5.1, C8.2, C9.1, C10.2, C11.2, C12.2, C17.1, CAN_L1.S1 (SHIELD1), CAN_L1.S2 (SHIELD2), CAN_R1.S1 (SHIELD1), CAN_R1.S2 (SHIELD2), D1.2 (A), D2.1 (K), J1.1, J1.2, J2.3, J3.1, J4.1, J5.1, J7.1 (-), J8.1 (-), J9.1 (-), J10.1 (-), J11.1 (-), U8.2 (GND), U8.8 (RS), U9.2, U10.3 (GND), U10.7 (A0); also elsewhere on the board
unnamed: D2.2 (A), R5.2
unnamed: C7.1, R3.1, U10.1 (IN+)
unnamed: C7.2, R2.1, U10.2 (IN-)
unnamed: C10.1, C11.1, U9.3, U$1.1
RESET: J5.2; also elsewhere on the board
SCL: J2.1, R28.2, U10.5 (SCL); also elsewhere on the board
SDA: J2.2, R27.2, U10.6 (SDA); also elsewhere on the board
STOP: J3.2; also elsewhere on the board

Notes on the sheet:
External power supply

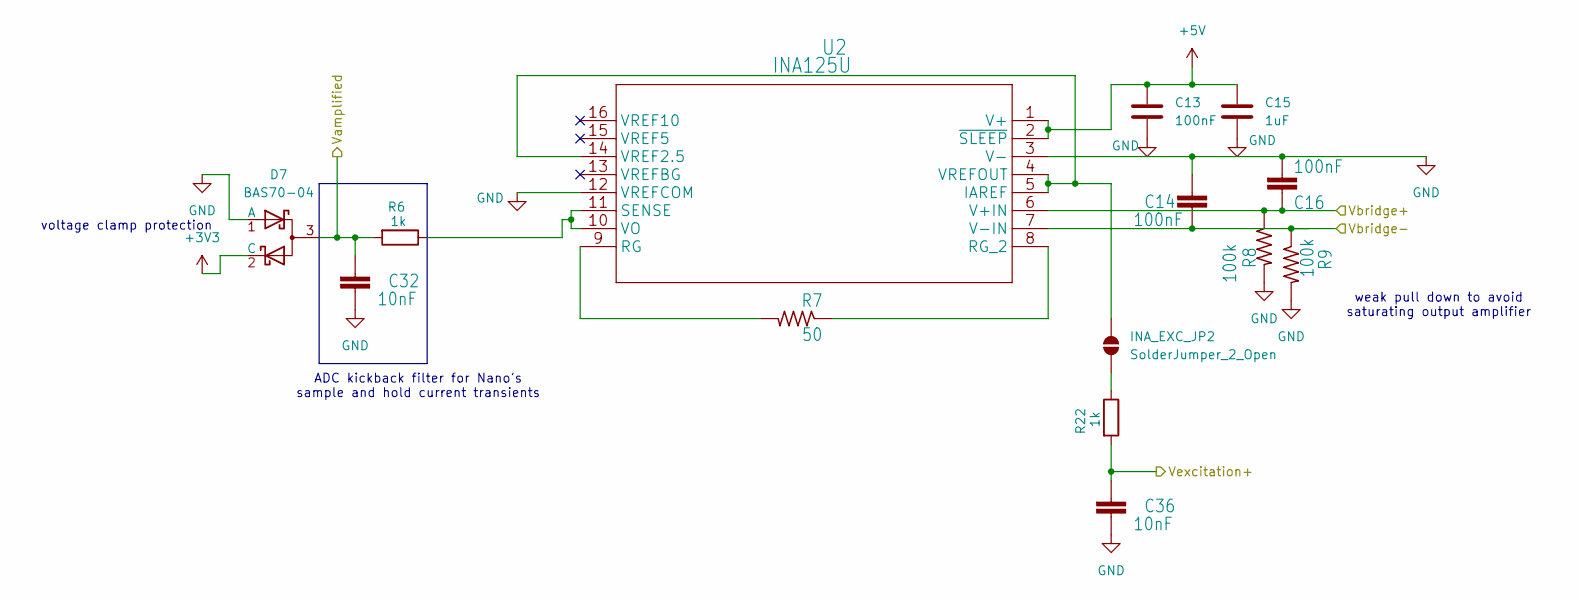
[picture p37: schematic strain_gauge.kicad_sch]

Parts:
C13, C14, C16: 100nF; C_0805_2012Metric_Pad1.18x1.45mm_HandSolder
C15: 1uF; C_0805_2012Metric_Pad1.18x1.45mm_HandSolder
C32, C36: 10nF; C_0805_2012Metric_Pad1.18x1.45mm_HandSolder
D7: BAS70-04; P200_SOT-23
INA_EXC_JP2: SolderJumper_2_Open; SolderJumper-2_P1.3mm_Open_RoundedPad1.0x1.5mm
R6, R22: 1k; R_0805_2012Metric_Pad1.20x1.40mm_HandSolder
R7: 50; R_0805_2012Metric_Pad1.20x1.40mm_HandSolder
R8, R9: 100k; R_0805_2012Metric_Pad1.20x1.40mm_HandSolder
U2: INA125U; D16

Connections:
+3V3: D7.2 (C); also elsewhere on the board
+5V: C13.1, C15.1, U2.1 (V+), U2.2 (~SLEEP); also elsewhere on the board
/Load cells/Left LC Amplifier 2 (label 2)/Vbridge+: C16.1, R8.1, U2.6 (V+IN); also elsewhere on the board
/Load cells/Left LC Amplifier 2 (label 2)/Vbridge-: C14.1, R9.1, U2.7 (V-IN); also elsewhere on the board
GND: C13.2, C14.2, C15.2, C16.2, C32.1, C36.1, D7.1 (A), R8.2, R9.2, U2.3 (V-), U2.12 (VREFCOM); also elsewhere on the board
L2_LC_N: C32.2, D7.3, R6.2; also elsewhere on the board
L2_LC_P: C36.2, R22.2; also elsewhere on the board
unnamed: INA_EXC_JP2.1 (A), U2.4 (VREFOUT), U2.5 (IAREF), U2.14 (VREF2.5)
unnamed: INA_EXC_JP2.2 (B), R22.1
unnamed: R7.2, U2.9 (RG)
unnamed: R7.1, U2.8 (RG_2)
unnamed: R6.1, U2.10 (VO), U2.11 (SENSE)

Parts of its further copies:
C18, C19, C21, C23, C24, C26, C28, C29, C31: 100nF; C_0805_2012Metric_Pad1.18x1.45mm_HandSolder
C20, C25, C30: 1uF; C_0805_2012Metric_Pad1.18x1.45mm_HandSolder
C33, C34, C35, C37, C38, C39: 10nF; C_0805_2012Metric_Pad1.18x1.45mm_HandSolder
D8, D9, D10: BAS70-04; P200_SOT-23
INA_EXC_JP1, INA_EXC_JP3, INA_EXC_JP4: SolderJumper_2_Open; SolderJumper-2_P1.3mm_Open_RoundedPad1.0x1.5mm
R10, R14, R18, R23, R24, R25: 1k; R_0805_2012Metric_Pad1.20x1.40mm_HandSolder
R11, R15, R19: 50; R_0805_2012Metric_Pad1.20x1.40mm_HandSolder
R12, R13, R16, R17, R20, R21: 100k; R_0805_2012Metric_Pad1.20x1.40mm_HandSolder
U1, U3, U4: INA125U; D16

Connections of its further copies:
+3V3: D8.2 (C), D9.2 (C), D10.2 (C); also elsewhere on the board
+5V: C18.1, C20.1, C23.1, C25.1, C28.1, C30.1, U1.1 (V+), U1.2 (~SLEEP), U3.1 (V+), U3.2 (~SLEEP), U4.1 (V+), U4.2 (~SLEEP); also elsewhere on the board
/Load cells/Left LC Amplifier 1 (label 1)/Vbridge+: C21.1, R12.1, U1.6 (V+IN); also elsewhere on the board
/Load cells/Left LC Amplifier 1 (label 1)/Vbridge-: C19.1, R13.1, U1.7 (V-IN); also elsewhere on the board
/Load cells/Right LC Amplifier 2 (label 4)/Vbridge+: C26.1, R16.1, U4.6 (V+IN); also elsewhere on the board
/Load cells/Right LC Amplifier 2 (label 4)/Vbridge-: C24.1, R17.1, U4.7 (V-IN); also elsewhere on the board
/Load cells/Right LC Amplifier 1 (label 3)/Vbridge+: C31.1, R20.1, U3.6 (V+IN); also elsewhere on the board
/Load cells/Right LC Amplifier 1 (label 3)/Vbridge-: C29.1, R21.1, U3.7 (V-IN); also elsewhere on the board
GND: C18.2, C19.2, C20.2, C21.2, C23.2, C24.2, C25.2, C26.2, C28.2, C29.2, C30.2, C31.2, C33.1, C34.1, C35.1, C37.1, C38.1, C39.1, D8.1 (A), D9.1 (A), D10.1 (A), R12.2, R13.2, R16.2, R17.2, R20.2, R21.2, U1.3 (V-), U1.12 (VREFCOM), U3.3 (V-), U3.12 (VREFCOM), U4.3 (V-), U4.12 (VREFCOM); also elsewhere on the board
L1_LC_N: C33.2, D8.3, R10.2; also elsewhere on the board
L1_LC_P: C37.2, R23.2; also elsewhere on the board
unnamed: INA_EXC_JP1.1 (A), U1.4 (VREFOUT), U1.5 (IAREF), U1.14 (VREF2.5)
unnamed: INA_EXC_JP1.2 (B), R23.1
unnamed: INA_EXC_JP3.1 (A), U3.4 (VREFOUT), U3.5 (IAREF), U3.14 (VREF2.5)
unnamed: INA_EXC_JP3.2 (B), R25.1
unnamed: INA_EXC_JP4.1 (A), U4.4 (VREFOUT), U4.5 (IAREF), U4.14 (VREF2.5)
unnamed: INA_EXC_JP4.2 (B), R24.1
unnamed: R11.2, U1.9 (RG)
unnamed: R11.1, U1.8 (RG_2)
unnamed: R10.1, U1.10 (VO), U1.11 (SENSE)
unnamed: R19.2, U3.9 (RG)
unnamed: R19.1, U3.8 (RG_2)
unnamed: R18.1, U3.10 (VO), U3.11 (SENSE)
unnamed: R15.2, U4.9 (RG)
unnamed: R15.1, U4.8 (RG_2)
unnamed: R14.1, U4.10 (VO), U4.11 (SENSE)
R1_LC_N: C35.2, D10.3, R18.2; also elsewhere on the board
R1_LC_P: C39.2, R25.2; also elsewhere on the board
R2_LC_N: C34.2, D9.3, R14.2; also elsewhere on the board
R2_LC_P: C38.2, R24.2; also elsewhere on the board

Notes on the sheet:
voltage clamp protection
weak pull down to avoid saturating output amplifier
ADC kickback filter for Nano's sample and hold current transients

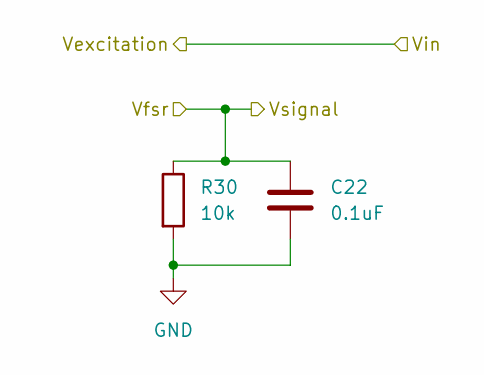
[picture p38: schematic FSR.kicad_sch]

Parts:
C22: 0.1uF; C_0805_2012Metric_Pad1.18x1.45mm_HandSolder
R30: 10k; R_0805_2012Metric_Pad1.20x1.40mm_HandSolder

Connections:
FSR_1_IN: C22.1, R30.1; also elsewhere on the board
GND: C22.2, R30.2; also elsewhere on the board

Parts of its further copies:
C6: 0.1uF; C_0805_2012Metric_Pad1.18x1.45mm_HandSolder
R29: 10k; R_0805_2012Metric_Pad1.20x1.40mm_HandSolder

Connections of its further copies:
FSR_2_IN: C6.1, R29.1; also elsewhere on the board
GND: C6.2, R29.2; also elsewhere on the board

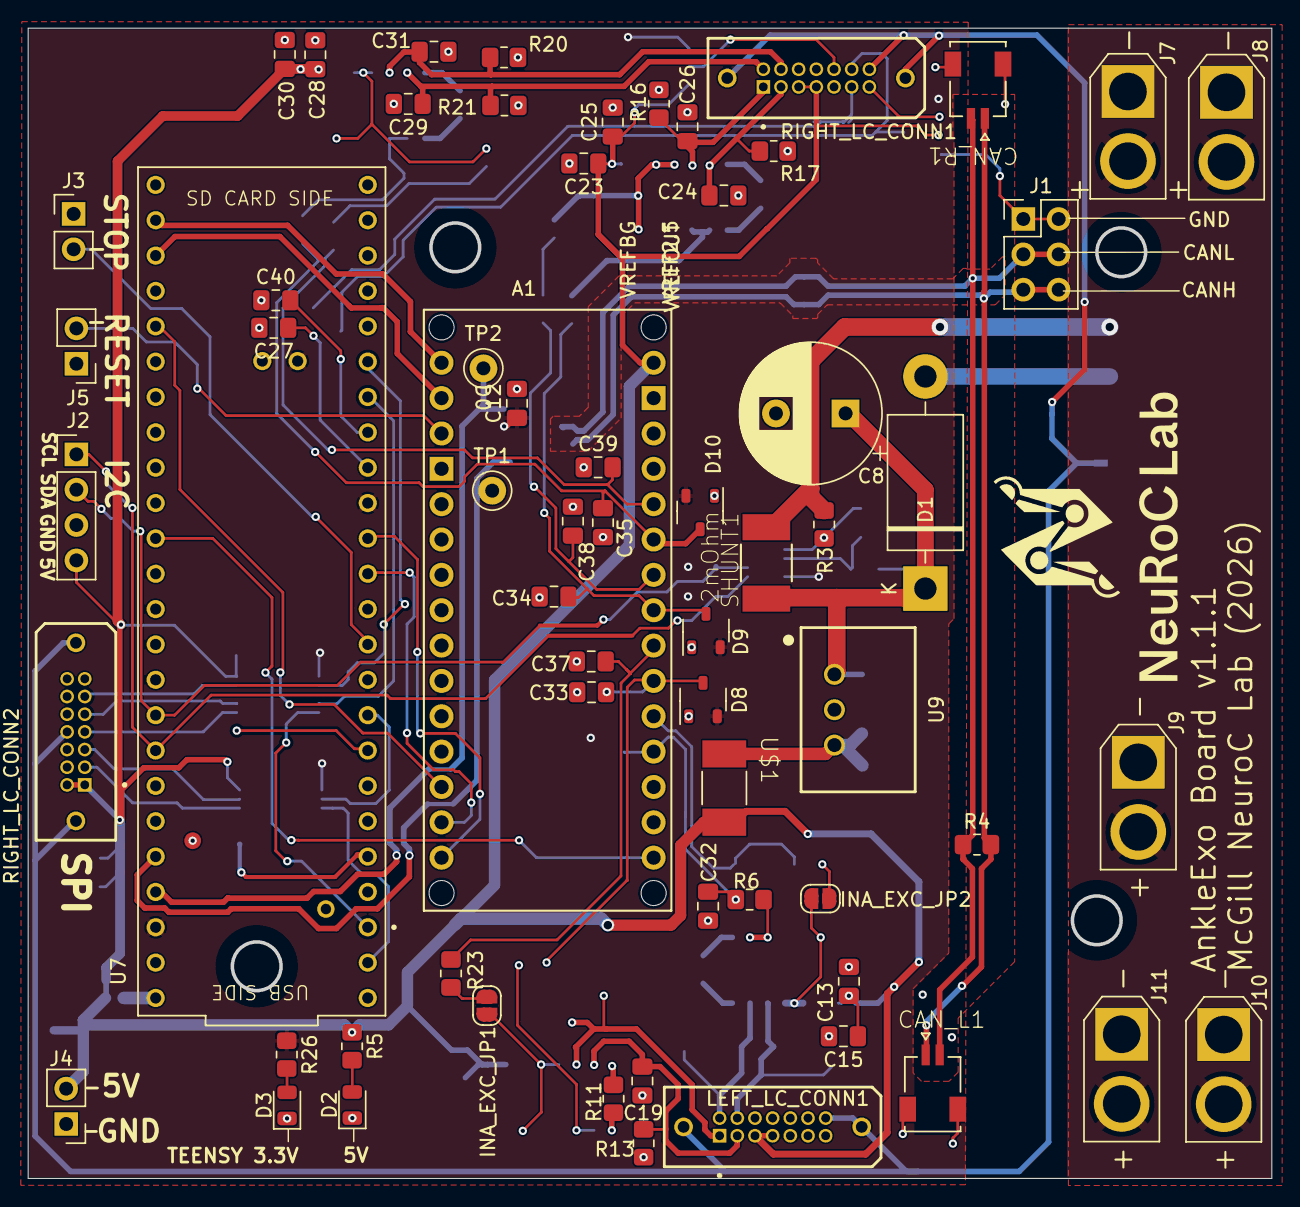
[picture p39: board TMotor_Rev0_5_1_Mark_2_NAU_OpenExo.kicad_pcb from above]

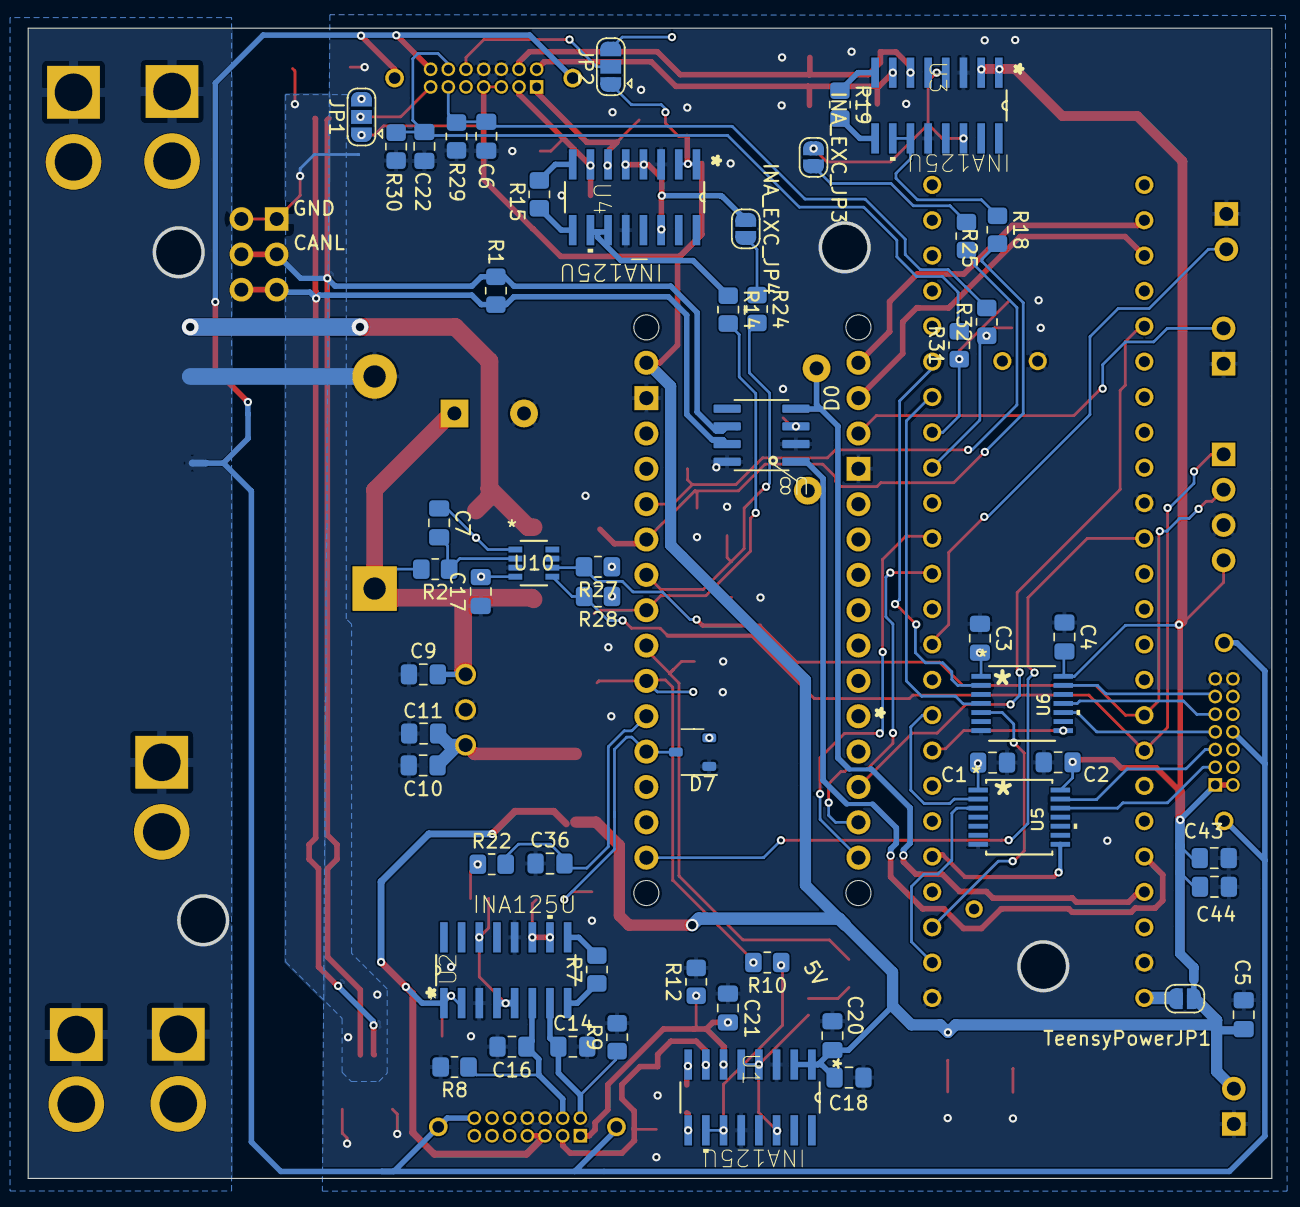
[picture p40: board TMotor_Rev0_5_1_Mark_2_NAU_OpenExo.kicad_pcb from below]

Board: 2 copper layers, 89.4 x 82.6 mm, 119 parts (55 on the bottom side), 80 nets.

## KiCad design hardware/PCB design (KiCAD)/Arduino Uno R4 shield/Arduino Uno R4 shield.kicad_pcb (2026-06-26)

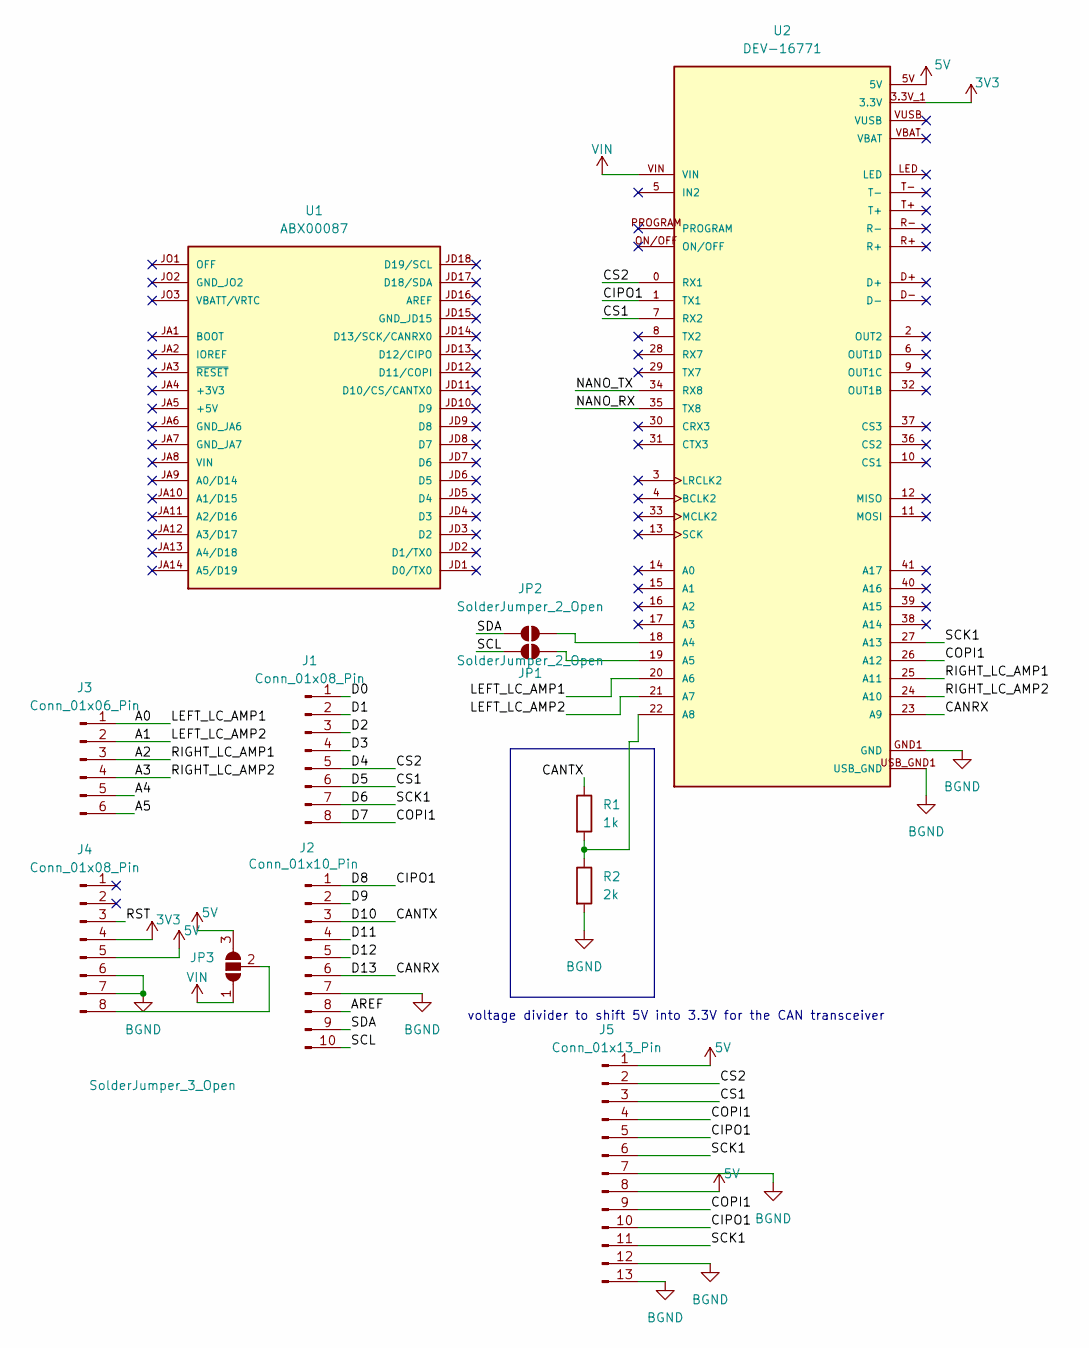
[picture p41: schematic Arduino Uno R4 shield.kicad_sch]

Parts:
J1, J4: Conn_01x08_Pin; PinHeader_1x08_P2.54mm_Vertical
J2: Conn_01x10_Pin; PinHeader_1x10_P2.54mm_Vertical
J3: Conn_01x06_Pin; PinHeader_1x06_P2.54mm_Vertical
J5: Conn_01x13_Pin; PinHeader_1x13_P2.54mm_Vertical
JP1, JP2: SolderJumper_2_Open; SolderJumper-2_P1.3mm_Open_RoundedPad1.0x1.5mm
JP3: SolderJumper_3_Open; SolderJumper-3_P1.3mm_Open_Pad1.0x1.5mm_NumberLabels
R1: 1k; R_Axial_DIN0207_L6.3mm_D2.5mm_P10.16mm_Horizontal
R2: 2k; R_Axial_DIN0207_L6.3mm_D2.5mm_P10.16mm_Horizontal
U1: ABX00087; MODULE_ABX00087; PARTREV 4
U2: DEV-16771; MODULE_DEV-16771; PARTREV 4.1

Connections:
3V3: J4.4, U2.3.3V_1 (3.3V), U2.3.3V_2 (3.3V), U2.3.3V_3 (3.3V)
5V: J4.5, J5.1, J5.8, JP3.3 (B), U2.5V
/A0: J3.1, U2.20 (A6)
/A1: J3.2, U2.21 (A7)
/A2: J3.3, U2.25 (A11)
/A3: J3.4, U2.24 (A10)
/A4: J3.5
/A5: J3.6
/AREF: J2.8
/CANRX: J2.6, U2.23 (A9)
/CANTX: J2.3, R1.1
/CIPO1: J2.1, J5.5, J5.10, U2.1 (TX1)
/COPI1: J1.8, J5.4, J5.9, U2.26 (A12)
/CS1: J1.6, J5.3, U2.7 (RX2)
/CS2: J1.5, J5.2, U2.0 (RX1)
/D0: J1.1
/D1: J1.2
/D2: J1.3
/D3: J1.4
/D6: J1.7, J5.6, J5.11, U2.27 (A13)
/D9: J2.2
/D11: J2.4
/D12: J2.5
/NANO_RX: U2.35 (TX8)
/NANO_TX: U2.34 (RX8)
/RST: J4.3
/SCL: J2.10, JP1.1 (A)
/SDA: J2.9, JP2.1 (A)
BGND: J2.7, J4.6, J4.7, J5.7, J5.12, J5.13, R2.2, U2.GND1 (GND), U2.GND2 (GND), U2.GND3 (GND), U2.GND4 (GND), U2.GND5 (GND), U2.USB_GND1 (USB_GND), U2.USB_GND2 (USB_GND)
unnamed: J4.8, JP3.2 (C)
unnamed: JP1.2 (B), U2.19 (A5)
unnamed: JP2.2 (B), U2.18 (A4)
unnamed: R1.2, R2.1, U2.22 (A8)
VIN: JP3.1 (A), U2.VIN

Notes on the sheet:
voltage divider to shift 5V into 3.3V for the CAN transceiver

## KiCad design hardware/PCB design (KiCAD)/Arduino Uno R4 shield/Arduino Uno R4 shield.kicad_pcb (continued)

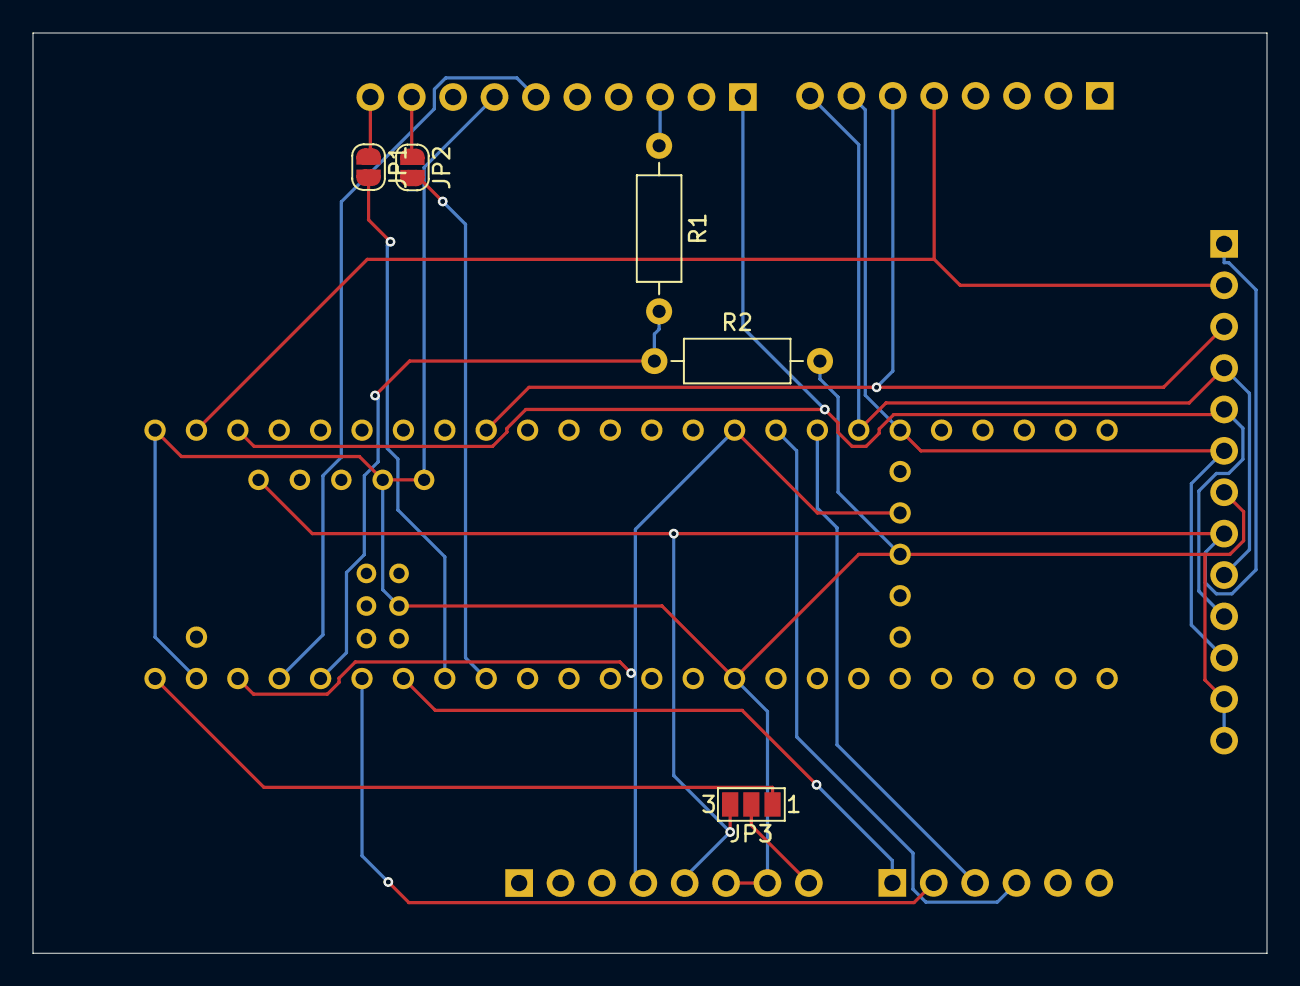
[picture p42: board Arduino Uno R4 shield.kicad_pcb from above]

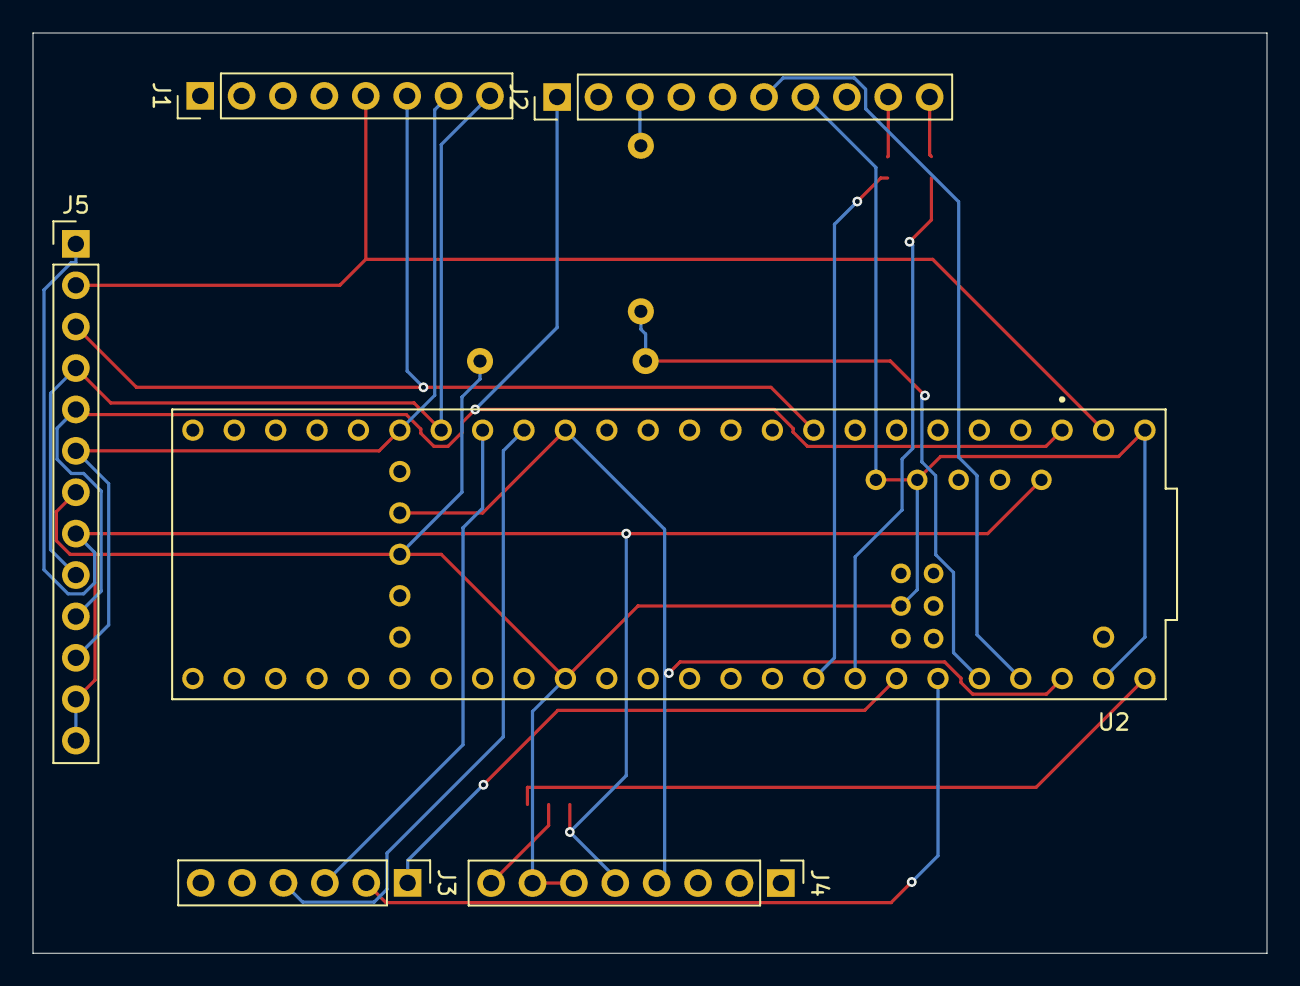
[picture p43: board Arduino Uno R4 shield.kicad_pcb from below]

Board: 2 copper layers, 75.7 x 56.5 mm, 11 parts (6 on the bottom side), 21 nets.

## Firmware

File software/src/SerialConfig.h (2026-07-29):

//
// Created by Oscar Tesniere on 20/07/2026.
//

#pragma once

#include <Arduino.h>

namespace TelemetryKey {

     constexpr char LeftLoadCell1[]  = "LLC1";
     constexpr char LeftLoadCell2[]  = "LLC2";
     constexpr char RightLoadCell1[] = "RLC1";
     constexpr char RightLoadCell2[] = "RLC2";

     constexpr char Motors[]    = "MOTORS";
     constexpr char MotorId[]   = "MTR_ID_DEC";
     constexpr char MotorPos[]  = "MTR_POS_RAD";
     constexpr char MotorVel[]  = "MTR_VEL_RADS";
     constexpr char MotorTrq[]  = "MTR_TRQ_NM";
     constexpr char MotorErr[]  = "MTR_ERR_DEC";
     constexpr char MotorTemp[] = "MTR_TEMP_DEG";

     constexpr char LeftEncoder[]  = "LENC";
     constexpr char RightEncoder[] = "RENC";

}

// could have used #DEFINE directives here as well ....
// maybe do a Telemetry data class as well ?

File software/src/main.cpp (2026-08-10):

//
// Created by Oscar Tesniere on 17/07/2026.
// Integration script for interfacing both the motor, the
//

// This script will be used for the one-leg setup testing

// Here the Teensy will communicate with the Arduino through SPI as a temporary fix

#include <cstdint>
#include <cmath>

#include <Arduino.h>


#include "Board.h"
#include "SerialProtocol.h"

// very important check to avoid problems. Code should be compiled separately for the Teensy and the Nano.
#if defined(PLATFORM_TEENSY41) && defined(PLATFORM_NORDIC)
#error "You specified both PLATFORM_TEENSY41 and PLATFORM_NORDIC. Please select ONLY ONE platform to compile"
#endif

#if defined(PLATFORM_TEENSY41)

#include "Encoder.h"
#include "CANMotorMIT.h"
#include "MotorConfig.h"
#include "LoadCell.h"
#include <ArduinoJson.h>
//TODO TESTING ONLY REMOVE LATER
//#include "TransparentMode.h"

#elif defined(PLATFORM_NORDIC)

#include <ArduinoBLE.h>
#include <ArduinoJson.h>

#endif


// Load Cell configuration in version up to (and including) 1.1.0 and past (but including) 1.1.1

// ==================================== LOAD CELL CONFIGURATION =========================================
#include "LoadCell.h"
#if defined(PLATFORM_TEENSY41) && HW_VERSION_AT_MOST(1,1,0)

using LoadCellObj = LoadCell_Teensy41;
using LoadCellHandlerObj = LoadCellHandler_Teensy41;


#elif defined(PLATFORM_NORDIC) && HW_VERSION_AT_LEAST(1,1,1)
#pragma message "Enabling Arduino Nano ADC"

using LoadCellObj = LoadCell_NanoBLE;
using LoadCellHandlerObj = LoadCellHandler_NanoBLE;
#endif
#if defined(PLATFORM_NORDIC) && HW_VERSION_AT_LEAST(1,1,1) || defined(PLATFORM_TEENSY41) && HW_VERSION_AT_MOST(1,1,0)
LoadCellParams loadCellParams{};

LoadCellObj LC_L_1(
    loadCellParams,
    LoadCellId::Left1
);

LoadCellObj LC_L_2(
    loadCellParams,
    LoadCellId::Left2
);

LoadCellObj LC_R_1(
    loadCellParams,
    LoadCellId::Right1
);

LoadCellObj LC_R_2(
    loadCellParams,
    LoadCellId::Right2
);

LoadCell* loadCells[loadCellCount] = {
    &LC_L_1,
    &LC_L_2,
    &LC_R_1,
    &LC_R_2
};

float forceBuffer[loadCellCount]{};

LoadCellHandlerObj loadCellController(
    loadCells,
    loadCellCount,
    forceBuffer
);
#endif


#if defined(PLATFORM_TEENSY41)

MotorCmd motor1Cmd {
    .position = 0.0f,
    .velocity = 0.0f,
    .torque = 0.0f,
    .kp = 0.0f,
    .kd = 0.0f
};
// to change running and software constraints head to CANMotorMIT.h

Encoder encoders(true, false);

constexpr byte MOTOR_ID = 0x03;

DataPayload payload {};
CANMotorMIT_Teensy motor(MOTOR_ID, motorParams,motorSoftwareConstraints,motorRunningConstraints,payload,motor1Cmd,5);//NO_MOTOR_UPDATE);
CANMotorMIT_Handler motorHandler(motor,nullptr);

//TODO remove that later after Motor Handler class has been validated, but keep it for debugging in one leg setup
#include "SerialMotorControl.h"
SerialMotorControl serialControl(Serial, motor1Cmd, motor);

constexpr uint32_t TELEMETRY_PERIOD_US = 5000; // 20 ms = 50 Hz ; 5ms = 200Hz
unsigned long now = millis();
unsigned long previousSend = millis();

UARTHandler_Teensy uart(Serial8,motorHandler);

//TODO REMOVE LATER AS WE ARE DOING THIS FOR DEBUG HERE

//PDControl transparentController(motorHandler,loadCellController,1.0f,1.0f,100UL);
EncoderPositions positions;

void setup()
{
    uart.begin();
    Serial.println("Initializing UART communication with Nano");
    encoders.begin();

    Serial.begin(230400);
    Serial.println("Initializing Serial communication with the Arduino UNO R4");

    Serial8.begin(230400); // using Serial 8 here, not serial 1
    Serial.println("Initializing the motor in MIT mode");
    motorHandler.begin();
	delay(10);
    //motor.sendMessage(exitMotorMode);
     #if HW_VERSION_AT_MOST(1,1,0)
    Serial.println("Initializing Load Cell Controller (PCB version v1.1.0 and -)");
    loadCellController.begin();

    Serial.println(
        "Keep all load cells unloaded during calibration."
    );

    loadCellController.calibrateAllOffsets(100);
    delay(1000);
    Serial.println("Calibrated Load Cell offset");
    #endif
	//TODO DEBUG ONLY remove later
	//transparentController.begin();
	//Serial.println("Started Transparent Mode controller");
}

uint32_t previousUpdate = micros();

void loop()
{
	//transparentController.update();
    uart.update();
    motor.update();
    serialControl.update();
    //delay(10); //TODO try to remove that unless it blocks the motor control update. This will ensure our data rate is set by TELEMETRY_PERIOD_US
    static uint32_t previousSend = 0;
    const uint32_t now = micros();
    positions = encoders.getPositions();
    Serial.print(positions.right_position);
    Serial.print(" .  ");
    Serial.println(positions.left_position);

    // to debug : the Teensy will stream data to your laptop through USB Serial, using ArduinoJSON for ease of unpacking
    #if defined(DEBUG)
    #pragma message "DEBUG mode is enabled, streaming data from Teensy to computer with ArduinoJSON"
    JsonDocument doc = createTelemetryPacket();
    serializeJson(doc, Serial);
    Serial.write('\n');
    #else
    if (now - previousSend >= TELEMETRY_PERIOD_US) {
        previousSend = micros();

        #if HW_VERSION_AT_MOST(1,1,0)
        // versions before and up to v1.1.0 : sample the load cells from the Teensy
        const float* forces = loadCellController.sampleAll();
        LoadCellVoltages loadCells {
            forces[0],
            forces[1],
            forces[2],
            forces[3],
        };
        if(forces[0]>80.0f || forces[1]>80.0f || forces[2]>80.0f || forces[3]>80.0f){
            Serial.println("INVALID LOAD CELL DATA");
        }
        #else
        // versions above (and including) v1.1.1 : leave it up to the Arduino Nano to populate the load cell voltages
        LoadCellVoltages loadCells {
            0.0f,
            0.0f,
            0.0f,
            0.0f,
        };
        #endif

         payload = {
            loadCells,
            positions,
            motor.m_reply,
        };

        uart.send(payload);

    }
    #endif

}
#elif defined(PLATFORM_NORDIC)

DataPayload payload {};
UARTHandler_Nano uart(Serial1,payload); //TODO ideally later on pass on reference to BLEHandler so it follows the same semantics as in UARTController uart(Serial8,motorHandler);

BLEHandler ble(
    payload,
    uart
);

void setup(){
    //randomSeed(analogRead(A0));
    delay(1000); // add a delay because sometimes the Serial connection takes more time to be established and the arduino code has already moved on to execution of loop
    Serial.begin(230400);
    uart.begin();
    Serial1.begin(230400);
    delay(1000);

    while (Serial1.available() > 0) {
        Serial1.read();
    }
    Serial.println("Starting Arduino Nano script");
    #if HW_VERSION_AT_LEAST(1,1,1)
    Serial.println("Initializing Arduino Nano LoadCell Handler (PCB v1.1.1+)");
    loadCellController.begin();
    loadCellController.calibrateAllOffsets(100);
    Serial.println("Do not move the load cells ! Calibration in progress");
    delay(1000);
    #endif
    if(!ble.begin()){
    Serial.println("BLE Initialization failed. Aborting");
    while(1){}
    }
    Serial.println("BLE initialization successful");
}

void loop(){
    /*
    WHEN NOT RUNNING THE TEENSY (I.E NANO AND COMPUTER ALONE) COMMENT THIS
    // TODO ADD A CHECK LIKE Serial1.available() to check if the teensy is actually sending valid and updated data
    while(readPayload(ble.m_payload,Serial1))
    { // Serial1 is the UART port used by the Arduino Nano
        ble.update(); // update the "bulletin board" on bluetooth
    }
    */
    // Read one complete payload from the Teensy.
    uart.update();
    /*
    if(payload.loadCells.LeftLoadCell1>80.0f || payload.loadCells.LeftLoadCell2>80.0f || payload.loadCells.RightLoadCell1>80.0f || payload.loadCells.RightLoadCell2>80.0f){
        Serial.print("INVALID LOAD CELL DATA  : ");
        Serial.print(payload.loadCells.LeftLoadCell1);
        Serial.print("   ");
        Serial.print(payload.loadCells.LeftLoadCell2);
        Serial.print("   ");
        Serial.print(payload.loadCells.RightLoadCell1);
        Serial.print("   ");
        Serial.println(payload.loadCells.RightLoadCell2);
    }
    */

    #if HW_VERSION_AT_LEAST(1,1,1)
    // version v1.1.1 and onwards : the Arduino Nano is the one sampling the load cell voltages so it directly modifies the payload object sent from the Teensy before posting it on BLE
    const float* forces = loadCellController.sampleAll();

    payload.loadCells = {
        forces[0],
        forces[1],
        forces[2],
        forces[3],
    };
    #endif

    #if defined(USING_BLE)
        ble.update();
    #endif

    #if defined(USING_SERIAL)
    JsonDocument doc = createTelemetryPacket(payload);
    serializeJson(doc, Serial);
    Serial.write('\n');
    #endif
}

#endif

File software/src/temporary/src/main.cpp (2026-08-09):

#include <Arduino.h>

#include "board.h"
#include "MessageBus.h"
#include "Driver.h"

template<size_t MaxTasks>
class Scheduler
{
public:
    bool add(ITask& task)
    {
        if (m_count >= MaxTasks) {
            return false;
        }

        m_tasks[m_count++] = &task;
        return true;
    }

    void run(uint32_t nowUs)
    {
        for (size_t i = 0;
             i < m_count;
             ++i)
        {
            m_tasks[i]->update(nowUs);
        }
    }

private:
    ITask* m_tasks[MaxTasks]{};
    size_t m_count{0};
};

Scheduler<12> scheduler;

#if defined(PLATFORM_TEENSY)

UARTHandler uart(
    board::teensy41::nanoUart
);

MessageBus messageBus(uart);

Topic<EncoderPositions> encoderTopic;
Topic<LoadCellForces> loadCellTopic;
Topic<MotorReply> leftMotorTopic;
Topic<PowerReadings> ina232Topic;
//Topic<MotorReply> rightMotorTopic;

RoutedTopic<
    EndpointId::EncoderSnapshot
> routedEncoderTopic(encoderTopic);

RoutedTopic<
    EndpointId::LoadCellSnapshot
> routedLoadCellTopic(loadCellTopic);

RoutedTopic<
    EndpointId::LeftMotorSnapshot
> routedLeftMotorTopic(leftMotorTopic);

RoutedTopic<
    EndpointId::Ina232Snapshot
> routedIna232Topic(ina232Topic);

/*RoutedTopic<
    EndpointId::RightMotorSnapshot
> routedRightMotorTopic(rightMotorTopic);
*/

EncoderDriver encoderDriver;

PollingPublisher<
    EncoderDriver,
    EndpointId::EncoderSnapshot,
    5'000
> encoderPublisher(
    encoderDriver,
    messageBus
);

INA232Driver ina232Driver;

PollingPublisher<
    INA232Driver,
    EndpointId::Ina232Snapshot,
    10'000
> ina232Publisher(
    ina232Driver,
    messageBus
);


CanBus canBus;

constexpr uint8_t LEFT_MOTOR_CAN_ID = 0x03;
constexpr uint8_t RIGHT_MOTOR_CAN_ID = 0x01;

// For compile testing, use the nominal limits.
// Replace these with your real software limits later.
AK60Params leftMotorLimits = MotorParams;
//AK60Params rightMotorLimits = MotorParams;

MotorDriver leftMotor(
    LEFT_MOTOR_CAN_ID,
    leftMotorLimits,
    canBus
);

/*
MotorDriver rightMotor(
    RIGHT_MOTOR_CAN_ID,
    rightMotorLimits,
    canBus
);
*/

class MotorCanReceiver final :
    public ITask
{
public:
    MotorCanReceiver(
        CanBus& bus,
        MotorDriver& left,/*
        MotorDriver& right,*/
        MessageBus& messageBus)
        : m_bus(bus),
          m_left(left),
          /*m_right(right),*/
          m_messageBus(messageBus)
    {}

    void update(uint32_t) override
    {
        CanFrame frame{};

        while (m_bus.read(frame))
        {
            if (m_left.accepts(frame))
            {
                m_messageBus.publish<
                    EndpointId::LeftMotorSnapshot
                >(
                    m_left.decode(frame)
                );
            }
            /*
            else if (
                m_right.accepts(frame))
            {
                m_messageBus.publish<
                    EndpointId::RightMotorSnapshot
                >(
                    m_right.decode(frame)
                );
            }
            */
        }
    }

private:
    CanBus& m_bus;
    MotorDriver& m_left;
    //MotorDriver& m_right;
    MessageBus& m_messageBus;
};

class MotorCommandTask : public ITask
{
public:
    explicit MotorCommandTask(
        MotorDriver& motor)
        : m_motor(motor)
    {}

    void update(uint32_t nowUs) override
    {
        static constexpr uint32_t
            PERIOD_US = 10'000; // 100 Hz

        if (nowUs - m_previousUs < PERIOD_US) {
            return;
        }

        m_previousUs += PERIOD_US;

        MotorCmd cmd{};

        // Safest possible MIT command:
        cmd.position = 0.0f;
        cmd.velocity = 0.0f;
        cmd.torque   = 0.0f;
        cmd.kp       = 0.0f;
        cmd.kd       = 0.0f;

        if (!m_motor.apply(cmd)) {
            Serial.println("Motor TX failed");
        }
    }

private:
    MotorDriver& m_motor;
    uint32_t m_previousUs{0};
};

MotorCanReceiver motorReceiver(
    canBus,
    leftMotor,
    //rightMotor,
    messageBus
);

MotorCommandTask leftMotorCommandTask(
    leftMotor
);

class DummyController final :
    public ITask
{
public:
    DummyController(
        Topic<EncoderPositions>& encoders,
        Topic<LoadCellForces>& loadCells,
        Topic<MotorReply>& leftMotor,
        Topic<PowerReadings>& power)
        : m_encoders(encoders),
          m_loadCells(loadCells),
          m_leftMotor(leftMotor),
          m_power(power)
    {}

    void update(uint32_t nowUs) override
    {
        static constexpr uint32_t
            PRINT_PERIOD_US = 100'000;

        if (nowUs - m_previousPrintUs <
            PRINT_PERIOD_US)
        {
            return;
        }

        m_previousPrintUs +=
            PRINT_PERIOD_US;

        Serial.println(
            "----- Distributed state -----"
        );

        printEncoder();
        printLoadCells();
        printMotor(
            "LEFT",
            m_leftMotor
        );
        printPower();
            /*
        printMotor(
            "RIGHT",
            m_rightMotor
        );
    */

        Serial.println();
    }
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

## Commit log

2026-06-15 Migrated project files to new
    [Arduino_Arduino_CAN.fzz, Arduino_Cubemars.fzz, Arduino_Teensy_CAN.fzz, wiring_Teensy.fzz]
2026-06-22 Updated AnkleDocs Documentation on the Mechanical Side
    [motor-mount.SLDPRT]
2026-06-22 Fix formatting of serial print statements
2026-06-22 Finish MIT Mode Motor Plotting Code (not tested yet)
2026-06-23 OOped the different components ; Moved KiCAD project to Github ; refactored website
    [Bill of Materials.csv, TMotor_Rev0_5_1_Mark_2_NAU_OpenExo.csv, TMotor_Rev0_5_1_Mark_2_NAU_OpenExo.kicad_pcb, TMotor_Rev0_5_1_Mark_2_NAU_OpenExo.kicad_sch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]
2026-06-24 Updated Motor Testing Code (works)
2026-06-24 Servo Mode Python Plotting Code Done
2026-06-25 fixed Servo mode class
2026-06-26 26/06 schematics updates
    see the changelog on the documentation /electrical/pcb
    [Arduino Uno R4 shield.kicad_pcb, Arduino Uno R4 shield.kicad_sch, TMotor_Rev0_5_1_Mark_2_NAU_OpenExo.kicad_pcb, TMotor_Rev0_5_1_Mark_2_NAU_OpenExo_1.kicad_sch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]
2026-06-28 Updated KiCAD for next iteration (some minor fixes) ; functional Servo controller and MIT is working over serial
    [TMotor_Rev0_5_1_Mark_2_NAU_OpenExo-Edge_Cuts.dxf, TMotor_Rev0_5_1_Mark_2_NAU_OpenExo-F_Courtyard.dxf, TMotor_Rev0_5_1_Mark_2_NAU_OpenExo.kicad_pcb, TMotor_Rev0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]
2026-06-29 Update velocity logging to include filtered values
